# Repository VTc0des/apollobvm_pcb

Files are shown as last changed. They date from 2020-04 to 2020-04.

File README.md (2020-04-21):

# Notes:
* Pause button on master has to go to digital pin 10 to allow for bootload.
* 47 uF caps on voltage regulator
* Diode on output from voltage regulator for programming
* Ground for programming port with labels
* Change to DPAK package for voltage regulator for better thermal properties
* Heat sync voltage regulator on ground plane

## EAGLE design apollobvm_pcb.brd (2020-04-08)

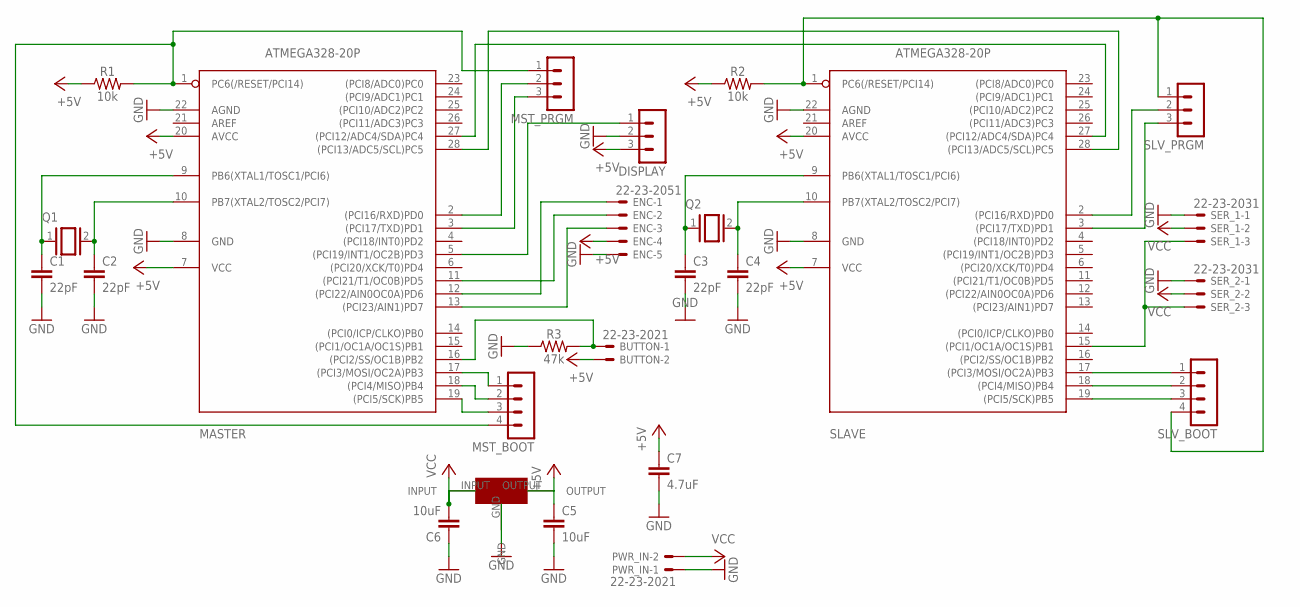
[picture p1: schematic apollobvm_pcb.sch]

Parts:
BUTTON: 22-23-2021
C1, C2, C3, C4: 22pF; 0603
C5, C6: 10uF; 0603
C7: 4.7uF; 0603
DISPLAY: MA03-1
ENC: 22-23-2051
MASTER: ATMEGA328-20P; DIL28-3
MST_BOOT: MA04-1
MST_PRGM: MA03-1
PWR_IN: 22-23-2021
Q1, Q2: XTAL/S; QS
R1, R2: 10k; 0603
R3: 47k; 0603
SER_1, SER_2: 22-23-2031
SLAVE: ATMEGA328-20P; DIL28-3
SLV_BOOT: MA04-1
SLV_PRGM: MA03-1
U$1: NCP1117

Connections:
+5V: BUTTON.2, C5.1, C7.1, DISPLAY.3, ENC.4, MASTER.7 (VCC), MASTER.20 (AVCC), R1.1, R2.1, SLAVE.7 (VCC), SLAVE.20 (AVCC), U$1.OUTPUT
GND: C1.2, C2.2, C3.2, C4.2, C5.2, C6.1, C7.2, DISPLAY.2, ENC.5, MASTER.8 (GND), MASTER.22 (AGND), PWR_IN.1, R3.1, SER_1.1, SER_2.1, SLAVE.8 (GND), SLAVE.22 (AGND), U$1.GND
unnamed: MASTER.1 (PC6(/RESET/PCI14)), MST_BOOT.4, MST_PRGM.1, R1.2
unnamed: R2.2, SLAVE.1 (PC6(/RESET/PCI14)), SLV_BOOT.4, SLV_PRGM.1
unnamed: C3.1, Q2.1, SLAVE.9 (PB6(XTAL1/TOSC1/PCI6))
unnamed: C4.1, Q2.2, SLAVE.10 (PB7(XTAL2/TOSC2/PCI7))
unnamed: C1.1, MASTER.9 (PB6(XTAL1/TOSC1/PCI6)), Q1.1
unnamed: C2.1, MASTER.10 (PB7(XTAL2/TOSC2/PCI7)), Q1.2
unnamed: SER_1.3, SER_2.3, SLAVE.15 ((PCI1/OC1A/OC1S)PB1)
unnamed: DISPLAY.1, MASTER.5 ((PCI19/INT1/OC2B)PD3)
unnamed: ENC.3, MASTER.13 ((PCI23/AIN1)PD7)
unnamed: ENC.2, MASTER.11 ((PCI21/T1/OC0B)PD5)
unnamed: MASTER.27 ((PCI12/ADC4/SDA)PC4), SLAVE.27 ((PCI12/ADC4/SDA)PC4)
unnamed: ENC.1, MASTER.12 ((PCI22/AIN0OC0A)PD6)
unnamed: MASTER.28 ((PCI13/ADC5/SCL)PC5), SLAVE.28 ((PCI13/ADC5/SCL)PC5)
unnamed: BUTTON.1, MASTER.16 ((PCI2/SS/OC1B)PB2), R3.2
unnamed: SLAVE.17 ((PCI3/MOSI/OC2A)PB3), SLV_BOOT.1
unnamed: SLAVE.18 ((PCI4/MISO)PB4), SLV_BOOT.2
unnamed: SLAVE.19 ((PCI5/SCK)PB5), SLV_BOOT.3
unnamed: MASTER.17 ((PCI3/MOSI/OC2A)PB3), MST_BOOT.1
unnamed: MASTER.18 ((PCI4/MISO)PB4), MST_BOOT.2
unnamed: MASTER.19 ((PCI5/SCK)PB5), MST_BOOT.3
unnamed: SLAVE.2 ((PCI16/RXD)PD0), SLV_PRGM.2
unnamed: SLAVE.3 ((PCI17/TXD)PD1), SLV_PRGM.3
unnamed: MASTER.2 ((PCI16/RXD)PD0), MST_PRGM.2
unnamed: MASTER.3 ((PCI17/TXD)PD1), MST_PRGM.3
VCC: C6.2, PWR_IN.2, SER_1.2, SER_2.2, U$1.INPUT

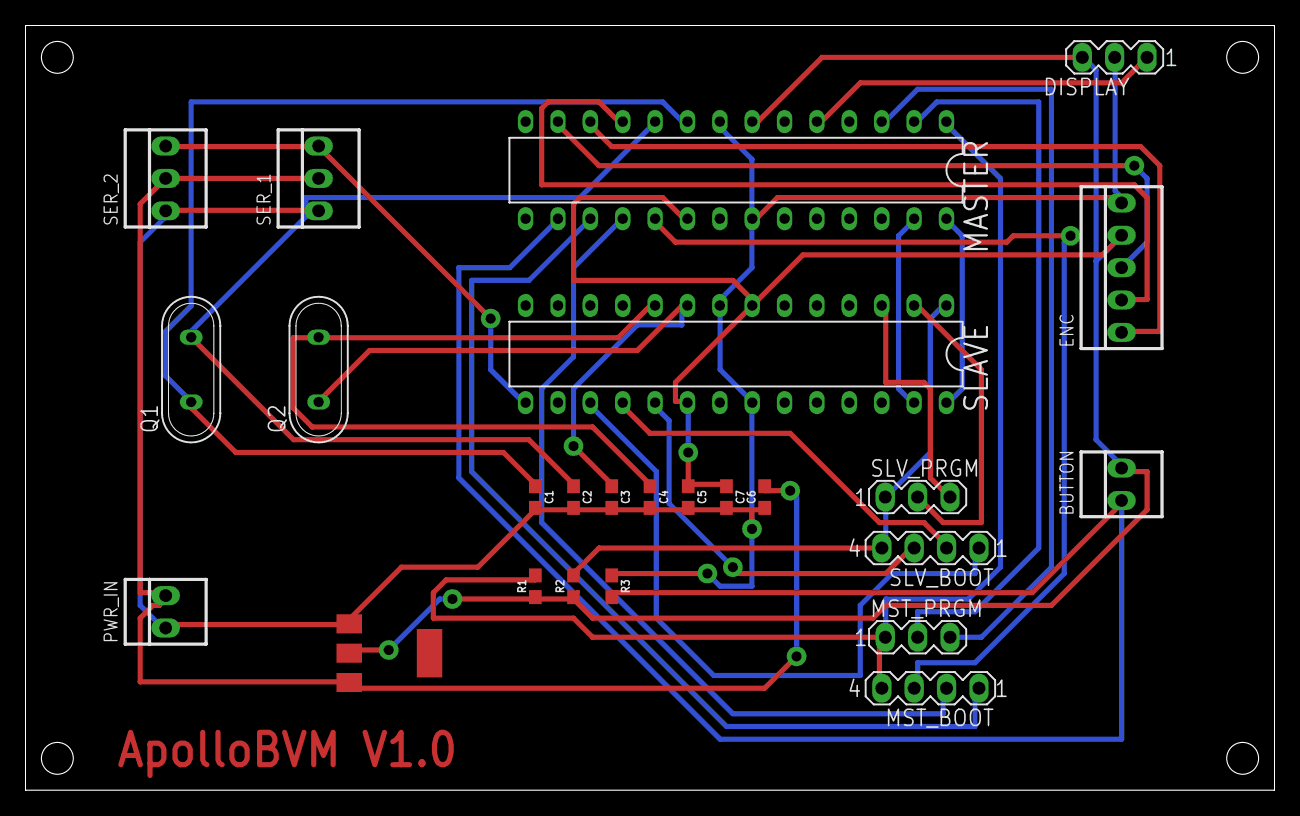
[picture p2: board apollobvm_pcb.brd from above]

Board: 2 copper layers, 98.0 x 60.0 mm, 25 parts (0 on the bottom side), 27 nets.

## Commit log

2020-04-08 Added initial schematic
    [apollobvm_pcb.brd]
2020-04-08 Added board file
2020-04-08 Finished initial board
    [apollobvm_pcb.sch]
2020-04-08 Fixed some final issues with initial board
    [apollobvm_pcb.brd]
2020-04-08 Moved PWM leads apart for servos
    [apollobvm_pcb.brd]

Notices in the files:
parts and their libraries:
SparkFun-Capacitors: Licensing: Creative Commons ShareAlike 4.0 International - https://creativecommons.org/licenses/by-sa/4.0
